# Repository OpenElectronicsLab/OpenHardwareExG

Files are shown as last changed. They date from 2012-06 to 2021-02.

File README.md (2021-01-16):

The OpenHardwareExG is a platform for ECG, EEG, EMG, ENG, EOG, and evoked potential applications.

[About OpenHardwareExG](http://openelectronicslab.github.io/OpenHardwareExG/)

The schematic can be found at:
[arduino-ads129x-schematic.pdf](./kicad-files/rev1/generated-files/arduino-ads129x-schematic.pdf)

History
-------
The OpenHardwareExG platform was originally developed as part of the
[eeg-mouse](https://github.com/OpenElectronicsLab/eeg-mouse) project.

Licences
--------
Hardware and Hardware Documentation License

CERN Open Hardware Licence

This applies to the kicad-files and scad-files directories.

"Documentation" means schematic diagrams, designs, circuit or circuit
board layouts, mechanical drawings, flow charts and descriptive text,
and other explanatory material that is explicitly stated as being made
available under the conditions of this Licence. The Documentation may be
in any medium, including but not limited to computer files and
representations on paper, film, or any other media.

Software License

GPL v3 or any later version

This applies to the OpenHardwareExG_firmware and src directories.

(The authors may be persuaded to license parts of their contributions
under another FOSS license if GPLv3 is a problem for integration with an
existing established project, for instance linux kernel is GPLv2. Please
contact us.)

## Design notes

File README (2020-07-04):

The OpenHardwareExG is a platform for ECG, EEG, EMG, ENG, EOG, and evoked potential applications.

http://openelectronicslab.github.io/OpenHardwareExG/

The OpenHardwareExG platform was originally developed as part of the eeg-mouse project.
https://github.com/OpenElectronicsLab/eeg-mouse

Software License

GPL v3 or any later version

(The authors may be persuaded to license parts of their contributions
under another FOSS license if GPLv3 is a problem for integration with an
existing established project, for instance linux kernel is GPLv2. Please
contact us.) Hardware and Hardware Documentation License

CERN Open Hardware Licence

(This applies mostly to the kicad-files and scad-files directories)
"Documentation" means schematic diagrams, designs, circuit or circuit
board layouts, mechanical drawings, flow charts and descriptive text,
and other explanatory material that is explicitly stated as being made
available under the conditions of this Licence. The Documentation may be
in any medium, including but not limited to computer files and
representations on paper, film, or any other media.

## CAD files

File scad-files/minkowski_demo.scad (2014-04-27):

// This demonstrates why we need to "translate" the origin of a rectangle
// before we apply a minkowski() transformation

// a rectangle with rounded corners of radius r
module rounded_rectangle(size = [1, 1], r = 0.1) {
    // move the origin, to compensate for shrinkage
    // comment out the translate to see the difference
    translate([r,r])

    minkowski() {
        square(size - 2*[r,r]);
        circle(r);
    }
}

$fn = 360;

rect= [3,5];

translate([3.1,0])
square(rect);

rounded_rectangle(rect, 1);

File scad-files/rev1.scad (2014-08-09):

// This file describes a rough 3d model of an OpenHardwareExG board with the
// analog and digital patch shields, along with the plastic fasteners used to
// hold the stack of boards together.  When run directly (vs included with
// "use") it will render the stack of rev1 boards.

include <rev1_dimensions.scad>

// a hexagonal prism with a distance d between sides
// handy for hex nuts
module hexprism(d=1, h=1) {
    $fn=6;
    cylinder(r=d/cos(30)/2, h=h);
}

// a hollow cylinder
module pipe(rout, rin, h) {
    difference() {
        cylinder(r=rout, h=h);
        translate([0, 0, -fudge]) cylinder(r=rin, h=h+2*fudge);
    }
}

// a plastic spacer between boards
module spacer() {
    black_plastic_color()
    pipe(spacer_outer_radius, spacer_inner_radius, spacer_height);
}

// a washer
module washer() {
    black_plastic_color()
    pipe(washer_outer_radius, washer_inner_radius, washer_height);
}

// a hex nut
module nut() {
    black_plastic_color()
    difference() {
        hexprism(d=nut_width, h=nut_height);
        translate([0, 0, -fudge])
            cylinder(r=nut_inner_radius, h=nut_height+2*fudge);
    }
}

// a socket-headed cap screw
module cap_screw(length = cap_screw_body_length) {
    black_plastic_color() {
        translate([0, 0, -cap_screw_cap_height])
        difference() {
            cylinder(r=cap_screw_cap_radius, h=cap_screw_cap_height);
            translate([0, 0, -1/3 * cap_screw_cap_height])
                hexprism(d=cap_screw_hex_key, h=cap_screw_cap_height);
        }
        cylinder(r=cap_screw_body_radius, h=length);
    }
}

// a touch-proof connector
module touch_proof_connector(_x, _y) {
    x = ( in1p_center_x + (_x * distance_between_touchproof_centers));
    y = ( in1p_center_y + (_y * distance_between_touchproof_centers));
    translate([x,y,-touchproof_projection])
        pipe(rout=touchproof_outer_radius, rin=touchproof_inner_radius,
            h=touchproof_height);
}

// color of the PCBs
module boardcolor() {
    color([0.3,0.3,0.3]) child();
}

// color of the black plastic components
module black_plastic_color() {
    for (i = [0 : $children-1])
        color([0.2,0.2,0.2]) child(i);
}

module drilled_hole(radius, x, y)
{
    translate([ x, y ])
        circle(r=radius);
}

module screw_hole(_x,_y)
{
    x = ( screw_hole_centers_x[_x]);
    y = ( screw_hole_centers_y[_y]);
    drilled_hole(screw_hole_radius, x, y);
}

module screw_holes()
{
    for( _y = [ 0 : 1 : 1 ] )
        for( _x = [ 0 : 1 : 3 ] )
            screw_hole(_x, _y);
}

// one of the PCBs
module board() {
    boardcolor() linear_extrude(height=board_thickness)
    difference() {
        square([board_length, board_width]);
        screw_holes();
    }

    // far Arduino headers
    black_plastic_color()
        translate([top_arduino_header_x, top_arduino_header_y,
            -top_arduino_header_height])
        cube([top_arduino_header_length, top_arduino_header_width,
            top_arduino_header_height]);

    // near Arduino headers
    black_plastic_color()
        translate([bottom_arduino_header_x, bottom_arduino_header_y,
            -bottom_arduino_header_height])
        cube([bottom_arduino_header_length, bottom_arduino_header_width,
            bottom_arduino_header_height]);
}

// the top-most PCB
module top_board() {
    board();

    // the touch-proof connectors
    for( _x = [ 0 : 1 : 7 ] ) {
        color([1,0.2,0.2]) touch_proof_connector(_x, 0);
        black_plastic_color() touch_proof_connector(_x, 1);
        black_plastic_color() touch_proof_connector(_x, 2);
        color([0.9,0.9,0.9]) touch_proof_connector(_x, 3);
    }
    color([0.2,0.5,0.2]) touch_proof_connector(8, 1.5);

    // the SPI header cap
    color([0.7,0.7,0.7])
        translate([spi_cap_x, spi_cap_y, -spi_cap_height])
        cube([spi_cap_length, spi_cap_width, spi_cap_height]);
    color([0.7,0.7,0.7])
        translate([spi_cap_tab_x, spi_cap_tab_y, -spi_cap_tab_height])
        cube([spi_cap_tab_length, spi_cap_tab_width, spi_cap_tab_height]);
}

module right_angle_header(pin_count, pitch, length, pin_width) {
    for( i = [ 1 : 1 : pin_count ] ) {
        color([0.9,0.9,0])
            translate([pitch/3,
                (i - 0.5) * pitch - pin_width/2,
                -pitch/2 - pin_width/2])
            cube([length - pitch/3, pin_width, pin_width]);
    }
    black_plastic_color() translate([pitch, 0, -pitch])
        cube([pitch, pin_count * pitch, pitch]);
}

// the bottom-most PCB
module bottom_board() {
    board();

    // USB connector
    color([0.7,0.7,0.7]) translate([USB_x, USB_y, -USB_height])
        difference() {
            cube([USB_length, USB_width, USB_height]);
            translate([USB_length/3, (USB_width - USB_hole_width)/2,
                (USB_height - USB_hole_height)/2])
                cube([USB_length, USB_hole_width, USB_hole_height]);
        }
    black_plastic_color() translate([USB_x, USB_y, -USB_height])
        translate([USB_length/3, (USB_width - USB_post_width)/2,
            (USB_height - USB_post_height)/2])
            cube([2/3*USB_length, USB_post_width, USB_post_height]);

    // FTDI header
    translate([FTDI_x, FTDI_y, 0])
        right_angle_header(FTDI_pin_count, FTDI_pitch, FTDI_length,
            FTDI_pin_width);

    // JYMCU header
    translate([JYMCU_x, JYMCU_y, 0])
        right_angle_header(JYMCU_pin_count, JYMCU_pitch, JYMCU_length,
            JYMCU_pin_width);
}

// the stack of all three boards mounted together
module board_stack() {
    top_board();
    translate([ 0, 0, board_thickness + spacer_height]) board();
    translate([ 0, 0, 2*board_thickness + 2*spacer_height]) bottom_board();
}

module fastener_stack(_x, _y) {
    x = ( screw_hole_centers_x[_x]);
    y = ( screw_hole_centers_y[_y]);
    translate([x,y,-washer_height]) cap_screw();
    translate([x,y,-washer_height]) washer();
    translate([x,y,board_thickness]) spacer();
    translate([x,y,2*board_thickness + spacer_height]) spacer();
    translate([x,y,3*board_thickness + 2*spacer_height]) washer();
    translate([x,y,washer_height + 3*board_thickness + 2*spacer_height]) nut();
}

translate([-board_length/2, board_width/2, 25]) rotate(a=[180,0,0]) {
    // the boards
    board_stack();

    // the fasteners
    for( _y = [ 0 : 1 : 1 ] )
        for( _x = [ 0 : 1 : 3 ] )
            fastener_stack(_x, _y);
}

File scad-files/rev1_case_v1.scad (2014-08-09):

// This file describes a laser-cut case for a rev1 OpenHardwareExG board with the
// analog and digital patch shields.  When run directly (vs included with
// "use") it will render an empty case and a case containing the rev1 boards.

include <rev1_case_v1_dimensions.scad>
use <rev1.scad>

// a rectangle with rounded corners of radius r
module rounded_rectangle(size = [1, 1], r = 0.1) {
    // move the origin, to compensate for shrinkage
    translate([r,r])
    minkowski() {
        square(size - 2*[r,r]);
        circle(r);
    }
}

// color of the case
module case_color() {
    transparency = 0.5;
    for (i = [0 : $children-1])
        color([0.5,0.5,0.7], transparency) child(i);
}

module drilled_slot(x, y, x_len, y_len, r=1)
{
    translate([ x + kerf/2, y + kerf/2 ])
        rounded_rectangle([x_len - kerf, y_len - kerf], r=max(0.01, r-kerf));
}

module drilled_hole(radius, x, y)
{
    translate([ x, y ])
        circle(r=radius - kerf/2);
}

// A slot for a tab, with semicircular cutouts for strain relief in the
// corners.
// note: the center of the slot is at (0,0) (to simplify reasoning about slots
// with different orientations)
module tab_slot(length, width, r_relief) {
    _length = length + tab_slot_length_allowance;
    translate([-_length/2 + kerf/2, -width/2 + kerf/2])
        square([_length - kerf, width - kerf]);
    translate([-_length/2, width/2])
        scale([1,-1]) rotate(90) tab_relief_notch();
    translate([-_length/2, -width/2])
        rotate(90) tab_relief_notch();
    translate([_length/2, width/2])
        rotate(270) tab_relief_notch();
    translate([_length/2, -width/2])
        scale([1,-1]) rotate(270) tab_relief_notch();
}

// A tab
// note: the base of the tab is at (0,0) (to simplify reasoning about tabs with
// different orientations)
module tab(length, width=tab_length, r_corner=tab_corner_radius) {
    union() {
        translate([-length/2 - kerf/2, -fudge]) {
            rounded_rectangle([length + kerf, width + kerf + fudge], r_corner);
            // square out the corners at the attachment point
            square([length + kerf, fudge + r_corner]);
        }
    }
}

// Relief cut outs for a tab.  These should be subtracted from the base part to
// minimize sharp interior angles that can concentrate stress and start crack
// formation.
module tab_relief(length) {
    union() {
        translate([-length/2, 0])
            scale([-1,-1]) tab_relief_notch();
        translate([length/2, 0])
            scale([1,-1]) tab_relief_notch();
    }
}

module tab_relief_notch() {
    difference() {
        union() {
            translate([kerf/2, -kerf/2 - fudge])
                square([(tab_relief_radius * 3) - kerf,
                        tab_relief_radius + kerf/2 + fudge]);
            translate([tab_relief_radius, tab_relief_radius])
                circle(tab_relief_radius - kerf/2);
        }
        translate([tab_relief_radius * 3, tab_relief_radius])
            circle(tab_relief_radius + kerf/2);
    }
}

module touch_proof_hole(_x, _y)
{
    x = ( in1p_center_x + (_x * distance_between_touchproof_centers));
    y = ( in1p_center_y + (_y * distance_between_touchproof_centers));
    drilled_hole(touchproof_outer_radius + touchproof_allowance/2, x, y);
}

module touch_proof_holes()
{
    for( _y = [ 0 : 1 : 3 ] )
        for( _x = [ 0 : 1 : 7 ] )
            touch_proof_hole(_x, _y);
    touch_proof_hole(8, 1.5);
}

module screw_hole(_x,_y)
{
    x = ( screw_hole_centers_x[_x]);
    y = ( screw_hole_centers_y[_y]);
    drilled_hole(screw_hole_radius, x, y);
}

module screw_holes()
{
    for( _y = [ 0 : 1 : 1 ] )
        for( _x = [ 0 : 1 : 3 ] )
            screw_hole(_x, _y);
}

module modified_android_shield_slots()
{
    drilled_slot(top_arduino_header_x - header_allowance/2,
        top_arduino_header_y - header_allowance/2,
        top_arduino_header_length + header_allowance,
        top_arduino_header_width + header_allowance,
        r=header_allowance/2);
    drilled_slot(bottom_arduino_header_x - header_allowance/2,
        bottom_arduino_header_y - header_allowance/2,
        bottom_arduino_header_length + header_allowance,
        bottom_arduino_header_width + header_allowance,
        r=header_allowance/2);
    drilled_slot(spi_cap_x - header_allowance/2,
        spi_cap_y - header_allowance/2,
        spi_cap_length + header_allowance,
        spi_cap_width + header_allowance,
        r=header_allowance/2);
    drilled_slot(spi_cap_tab_x - header_allowance/2,
        spi_cap_tab_y - header_allowance/2,
        spi_cap_tab_length + header_allowance,
        spi_cap_tab_width + header_allowance,
        r=header_allowance/2);
}

module vent_grid(length, width) {
    x_step = ((vent_radius*2) + vent_spacing);
    y_step = ((sqrt(3)/2) * ((vent_radius*2) + vent_spacing));

    num_x = 1 + floor((length - (vent_radius*2)) / x_step );
    num_y = 1 + floor((width - (vent_radius*2)) / y_step );
    translate([(length - (x_step * (num_x-1)))/2,
               (width  - (y_step * (num_y-1)))/2 ])
    for (j = [0 : num_y-1]) {
        for (i = [0 : num_x - 1 - (j - 2*floor(j / 2))]) {
            translate([(j - 2*floor(j / 2)) * (x_step/2), 0])
                translate([i * x_step, j * y_step])
                    circle(vent_radius - (kerf/2));
        }
    }
}

direction_x = [1,0];
direction_y = [0,1];

// Places children and the centers of a line of tabs starting from [0,0] and
// extending to a distance of length in direction direction.
module at_tab_centers(length, direction=direction_x) {
    // fit as many tabs as possible (assuming a gap on each side of the tabs)
    num_tabs = floor((length - tab_width) / (2*tab_width));
    // subtract out the tab widths to find the gap width.
    gap_width = (length - tab_width * num_tabs) / (num_tabs + 1);
    for (j = [0 : num_tabs-1]) {
        translate(direction*(gap_width + tab_width/2 + j*(tab_width + gap_width))) {
            for (i = [0 : $children-1]) {
                child(i);
            }
        }
    }
}

// the top/bottom with their shared holes
module top_blank() {
    difference() {
        translate([-case_top_margin - kerf/2, -case_top_margin - kerf/2])
            rounded_rectangle([ case_top_length + kerf, case_top_width + kerf ],
                case_top_corner_radius + kerf/2);
        screw_holes();

        // top row of tab slots
        translate([-air_gap, -air_gap - acrylic_thickness/2])
            at_tab_centers(board_length + 2 * air_gap, direction_x)
            tab_slot(tab_width,tab_slot_width,tab_slot_relief_radius);

        // bottom row of tab slots
        translate([-air_gap, board_width + air_gap + acrylic_thickness/2])
            at_tab_centers(board_length + 2 * air_gap, direction_x)
            tab_slot(tab_width,tab_slot_width,tab_slot_relief_radius);

        // left row of tab slots
        translate([-air_gap - acrylic_thickness/2, -case_top_margin])
            at_tab_centers(case_top_width, direction_y)
            rotate(90) tab_slot(tab_width,tab_slot_width,tab_slot_relief_radius);

        // right row of tab slots
        translate([ board_length + air_gap + acrylic_thickness/2,
            -case_top_margin])
            at_tab_centers(case_top_width, direction_y)
            rotate(90) tab_slot(tab_width,tab_slot_width,tab_slot_relief_radius);
    }
}

// the bottom
module bottom() {
    difference() {
        top_blank();
        translate([vent_bottom_margin,vent_bottom_margin])
        vent_grid(board_length - (2*vent_bottom_margin),
                         board_width - (2*vent_bottom_margin));
    }
}

// the top
module top() {
    difference() {
        top_blank();
        touch_proof_holes();
        modified_android_shield_slots();
    }
}

module front() {
    difference() {
        union() {
            // the basic rectangle
            translate([ -air_gap - kerf/2, - kerf/2])
                rounded_rectangle([ case_front_length + kerf,
                    case_front_width + kerf ],
                    case_front_corner_radius + kerf/2);

            // top tabs
            translate([-air_gap, 0])
                at_tab_centers(board_length + 2 * air_gap, direction_x)
                rotate(180) tab(tab_width, tab_length+compression_gap);

            // bottom tabs
            translate([-air_gap, case_front_width])
                at_tab_centers(board_length + 2 * air_gap, direction_x)
                tab(tab_width);

            // left tabs
            translate([-air_gap,
                       (-compression_gap/2)+(-tab_slot_length_allowance/4)])
                at_tab_centers(case_front_width, direction_y)
                rotate(90) tab(tab_width);

            // right tabs
            translate([board_length + air_gap,
                       (-compression_gap/2)+(-tab_slot_length_allowance/4)])
                at_tab_centers(case_front_width, direction_y)
                rotate(270) tab(tab_width);
        }
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

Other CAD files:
scad-files/rev1_case_v1_dimensions.scad
scad-files/rev1_case_v1_pattern.scad
scad-files/rev1_case_v1_pattern_P2.scad
scad-files/rev1_dimensions.scad

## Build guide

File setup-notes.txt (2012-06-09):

need to install the perl module Device/SerialPort.pm

    sudo apt-get install libdevice-serialport-perl

need to verify the /dev/ttyACM0 (or adjust serial-reader.pl to match)

need to have rights to tty device ("dialout" group on ubuntu)

sudo apt-get install gnuplot

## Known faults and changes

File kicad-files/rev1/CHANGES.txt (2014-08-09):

If you are distributing a modified version of the project, please use this file
to describe the dates and details of your modifications (as described in
section 3.3b of the CERN open hardware license).  If you are using a publicly
available repository to track changes (which we encourage), you may simply list
the URL of the repository here.

https://github.com/OpenElectronicsLab/OpenHardwareExG

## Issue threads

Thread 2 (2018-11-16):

### ISSUE TITLE
BoM list

### ISSUE THREAD

**Issue by hildogjr** [OpenElectronicsLab/OpenHardwareExG#2]
Missing some BoM list with the part number to make easy the purchase procedure.

**Comment by ericherman** [comment]
You can see a number of ".bom" files in the project. Probably you're interested in the main board, with the analog+digital patch shields:

 * https://github.com/OpenElectronicsLab/OpenHardwareExG/blob/master/kicad-files/rev1/arduino-ads129x.bom
 * https://github.com/OpenElectronicsLab/OpenHardwareExG/blob/master/kicad-files/rev1/patch-shield-analog.bom
 * https://github.com/OpenElectronicsLab/OpenHardwareExG/blob/master/kicad-files/rev1/patch-shield-digital.bom

Since there are multiple boards, we made a "combined mouser bom" for the patch-shield version for ordering from mouser:
 * https://github.com/OpenElectronicsLab/OpenHardwareExG/blob/master/kicad-files/rev1/combined.mouser.bom

However, not all parts were available from mouser at the time, as such we created a 4ucon bom:
 * https://github.com/OpenElectronicsLab/OpenHardwareExG/blob/master/kicad-files/rev1/4ucon.bom

Additionally, for the touch-proof panel mount jacks, we found them at DiscountDisposables as documented in:
 * https://github.com/OpenElectronicsLab/OpenHardwareExG/blob/master/kicad-files/rev1/fasteners.txt

I hope this is helpful for you.

**Comment by hildogjr** [comment]
Thanks

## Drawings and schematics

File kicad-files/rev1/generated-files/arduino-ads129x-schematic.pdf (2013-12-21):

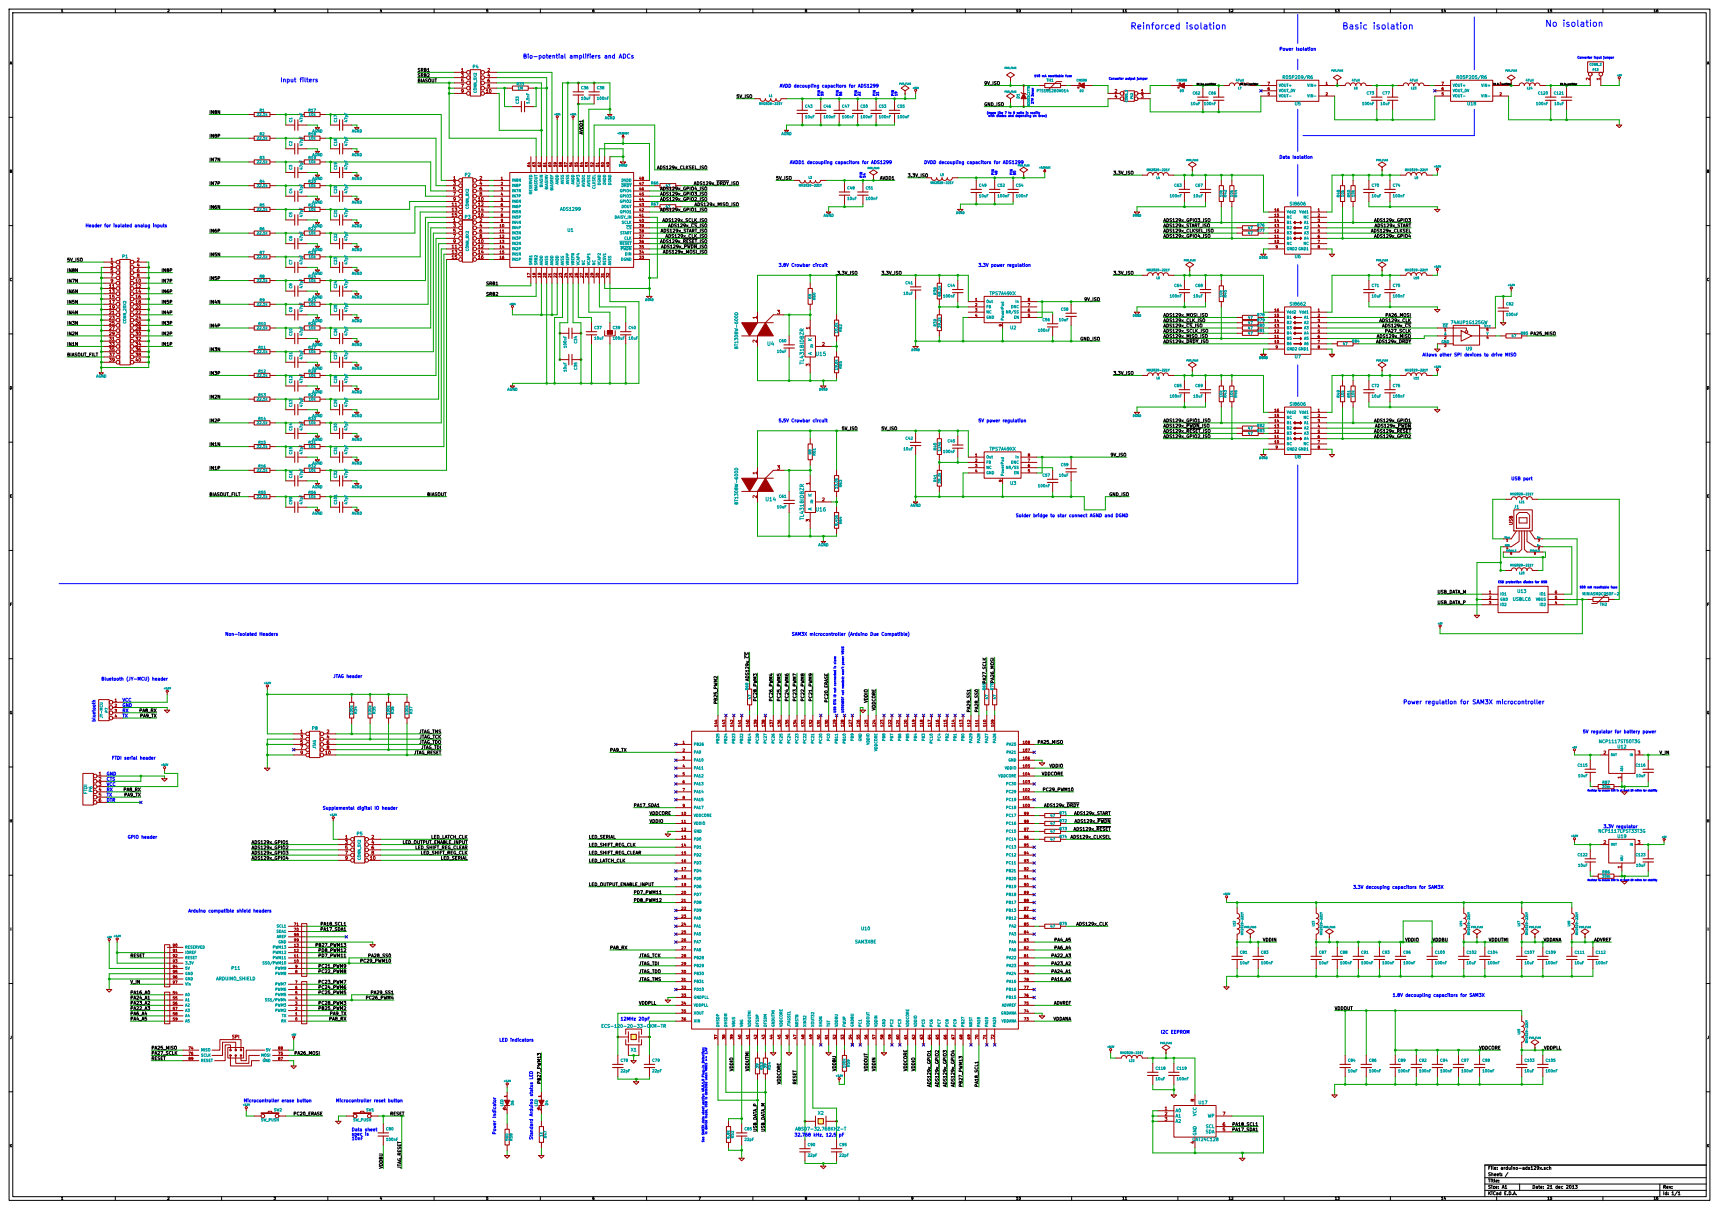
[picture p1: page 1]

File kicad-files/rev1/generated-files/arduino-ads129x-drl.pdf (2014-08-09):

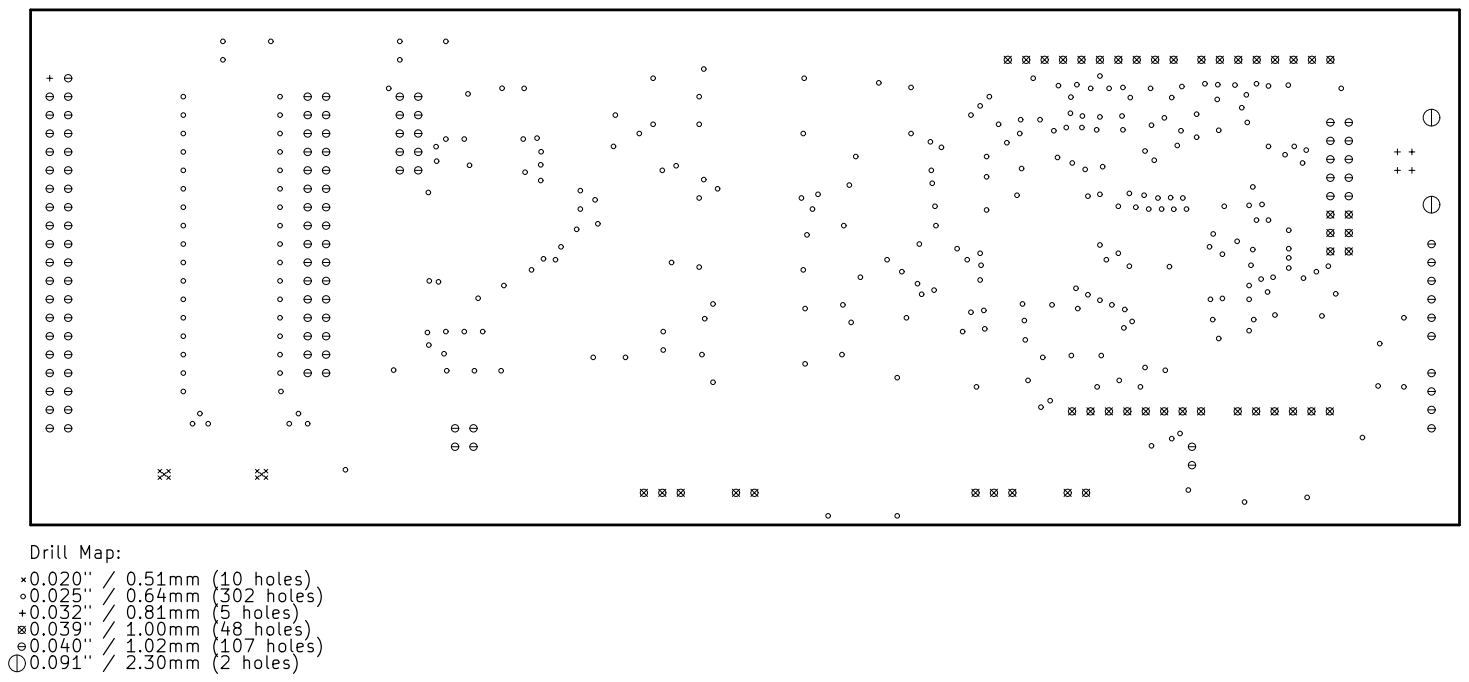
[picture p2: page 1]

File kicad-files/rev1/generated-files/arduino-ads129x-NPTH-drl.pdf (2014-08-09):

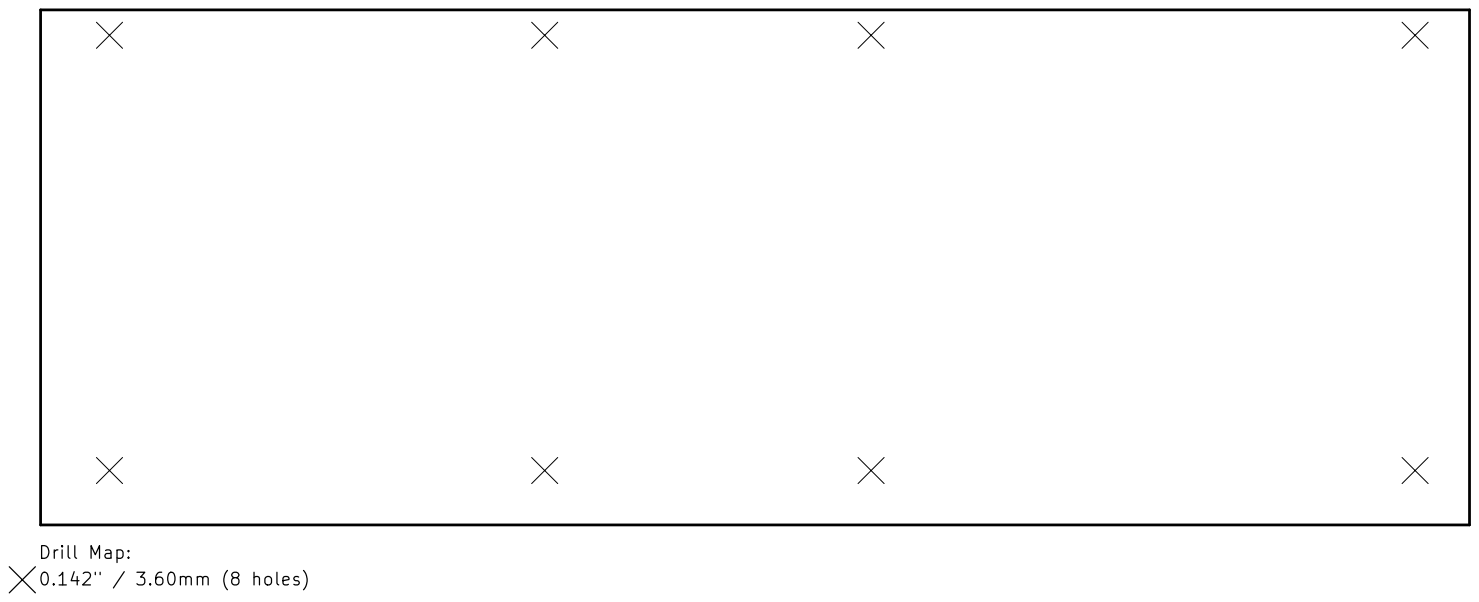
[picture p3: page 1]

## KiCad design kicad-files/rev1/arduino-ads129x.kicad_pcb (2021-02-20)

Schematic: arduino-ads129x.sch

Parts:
C1, C2, C3, C4, C5, C6, C7, C8, C9, C10, C11, C12, C13, C14, C15, C16, C17, C18, C19, C20, C21, C22, C23, C24, C25, C26, C27, C28, C29, C30, C31, C32, C99, C101: 270pF; SM0603
C33: 1.5nF; SM0603
C34, C38, C44, C45, C46, C47, C50, C51, C52, C53, C54, C55, C56, C57, C63, C64, C65, C66, C73, C74, C75, C76, C80, C82, C83, C86, C88, C89, C91, C92, C93, C94, C96, C97, C98, C100, C104, C105, C109, C112, C119, C120: 100nF; SM0603
C35, C36, C37, C40, C41, C42, C43, C48, C49, C60, C61, C67, C68, C69, C70, C71, C72, C77, C81, C84, C87, C102, C103, C107, C111, C115, C118, C121, C122, C123: 10uF; SM0805
C39: 100uF; SM2512
C58, C59, C62, C116: 10uF; SM1210
C78, C79, C85, C90, C95: 22pF; SM0603
D1: BZG03C27TR; DO214
D2, D3: CMS06; SM2010
D4, D6: LED; LED-0603
J1: USB; USB_B
L1, L2, L3, L4, L5, L6, L9, L10, L11, L12, L13, L14, L15, L17, L18, L20, L21, L22: MH2029-221Y; SM0805
L7, L8, L23, L24: 47uH; SRR4028
P1: CONN_20X2; PIN_ARRAY_20X2
P2, P3: CONN_8X2; pin_array_8x2
P4, P5: CONN_5X2; PIN_ARRAY_5x2
P6: FTDI; PIN_ARRAY-6X1
P7: JY-MCU; PIN_ARRAY_4x1
P8: JTAG; SMT_PIN_2x5
P11: ARDUINO_SHIELD; arduino_shield
P12: CONN_2; PIN_ARRAY_2X2
P13: CONN_2; PIN_ARRAY_2X1
R1, R2, R3, R4, R5, R6, R7, R8, R9, R10, R11, R12, R13, R14, R15, R16, R17, R18, R19, R20, R21, R22, R23, R24, R25, R26, R27, R28, R29, R30, R31, R32, R55, R56: 2.61k; SM0603
R33: 1M; SM0805
R34, R35, R36, R37, R59: 100k; SM0603
R38: 68.1k; SM0603
R39, R41: 39.2k; SM0603
R40: 124k; SM0603
R42, R43, R44, R45, R46, R48, R49, R50, R51: 10k; SM0603
R47: 1k; SM0603
R52: 6.8k; SM0603
R53, R54: 39; SM0603
R58: 560; SM0603
R60, R61: 68; SM0603
R62, R63: 10.0k; SM0603
R64: 8.45k; SM0603
R65: 19.6k; SM0603
R66, R67, R68, R69, R70, R71, R72, R73, R74, R75, R76, R77, R78, R79, R80, R81, R82, R83, R84, R85: 47; SM0603
R86, R87: 30m; SM0603
SW1, SW2: SW_PUSH; smt-tactile-button
TH1: PTS181260V014; SM1812
TH2: MINIASMDC050F-2; SM1812
U1: ADS1299; TQFP_64
U2, U3: TPS7A49XX; MSOP8_PowerPad
U4, U14: BT1308W-600D; SOT223
U5: R05P209/R6; SIP7_ISOLATOR
U6, U8: SI8606; SO16W
U7: SI8662; SO16W
U9: 74AUP1G125GW; SOT353
U10: SAM3X8E; TQFP144
U12: NCP1117ST50T3G; SOT223
U13: USBLC6; SOT23_6
U15, U16: TL431BIDBZR; SOT23
U17: CAT24C128; SOIC8
U18: R05P205/R6; SIP7_ISOLATOR
U19: NCP1117LPST33T3G; SOT223
X1: ECS-120-20-33-CKM-TR; smt-crystal-3.2x2.5
X2: ABS07-32.768KHZ-T; ABS07

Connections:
+3.3V: C82.1, C122.1, D6.1 (A), L9.2, L10.2, L11.2, L12.1, L13.1, L14.1, L17.1, L18.1, L22.1, P5.1, P6.3, P7.1, P8.1, P11.91, P11.93, R34.1, R35.1, R36.1, R37.1, R59.2, SW2.1, U9.5 (Vcc), U19.2 (OUT)
/3.3V_ISO: C41.1, C44.1, L3.2, L4.2, L5.2, L6.2, R38.1, R60.1, R62.1, U2.1 (Out), U4.1
/5V_ISO: C42.1, C45.1, L1.2, L2.2, P1.1, R40.1, R61.1, R63.1, U3.1 (Out), U14.1
/5V_in_prefilter: C120.1, C121.1, L24.1, P13.2 (PM)
/9V_ISO: C58.1, C59.1, D1.2 (K), TH1.1, U2.5 (EN), U2.8 (In), U3.5 (EN), U3.8 (In)
/9V_iso_postfilter: C62.1, C66.1, D3.1 (A), L7.2
/ADS129x_CLK: R75.2, U7.3 (A2)
/ADS129x_CLKSEL: R74.2, U6.5 (A3)
/ADS129x_CLKSEL_ISO: R77.1, U1.52 (CLKSEL)
/ADS129x_CLK_ISO: R79.1, U1.37 (CLK)
/ADS129x_GPIO1: P5.3, R51.2, U8.3 (A1), U10.64 (PC6)
/ADS129x_GPIO1_ISO: R43.2, U1.42 (GPIO1), U8.14 (B1)
/ADS129x_GPIO2: P5.5, R49.2, U8.6 (A4), U10.65 (PC7)
/ADS129x_GPIO2_ISO: R46.2, U1.44 (GPIO2), U8.11 (B4)
/ADS129x_GPIO3: P5.7, R50.2, U6.3 (A1), U10.66 (PC8)
/ADS129x_GPIO3_ISO: R42.2, U1.45 (GPIO3), U6.14 (B1)
/ADS129x_GPIO4: P5.9, R48.2, U6.6 (A4), U10.67 (PC9)
/ADS129x_GPIO4_ISO: R44.2, U1.46 (GPIO4), U6.11 (B4)
/ADS129x_MISO: U7.6 (A5), U9.2 (A)
/ADS129x_MISO_ISO: R45.2, R67.2, U7.11 (B5)
/ADS129x_MOSI_ISO: R78.1, U1.34 (DIN)
/ADS129x_SCLK_ISO: R81.1, U1.40 (SCLK)
/ADS129x_START: R71.2, U6.4 (A2)
/ADS129x_START_ISO: R76.1, U1.38 (START)
/ADS129x_~CS~: R68.2, U7.4 (A3), U9.1 (~OE~)
/ADS129x_~CS~_ISO: R80.1, U1.39 (~CS~)
/ADS129x_~DRDY~: R84.2, U10.100 (PC18)
/ADS129x_~DRDY~_ISO: R66.2, U7.10 (B6)
/ADS129x_~PWDN~: R72.2, U8.4 (A2)
/ADS129x_~PWDN~_ISO: R82.1, U1.35 (~PWDN~)
/ADS129x_~RESET~: R73.2, U8.5 (A3)
/ADS129x_~RESET~_ISO: R83.1, U1.36 (~RESET~)
/ADVREF: C111.1, C112.1, L18.2, U10.75 (ADVREF)
/AVDD1: C48.1, C51.1, L2.1, U1.54 (AVDD1)
/BIASOUT: C101.1, P4.5, P4.7, P4.9, R56.2, U1.63 (BIASOUT)
/BIASOUT_FILT: P1.37, R55.1
/IN1N: P1.33, R15.1
/IN1P: P1.34, R16.1
/IN2N: P1.29, R13.1
/IN2P: P1.30, R14.1
/IN3N: P1.25, R11.1
/IN3P: P1.26, R12.1
/IN4N: P1.21, R9.1
/IN4P: P1.22, R10.1
/IN5N: P1.17, R7.1
/IN5P: P1.18, R8.1
/IN6N: P1.13, R5.1
/IN6P: P1.14, R6.1
/IN7N: P1.9, R3.1
/IN7P: P1.10, R4.1
/IN8N: P1.5, R1.1
/IN8P: P1.6, R2.1
/JTAG_RESET: C80.1, P8.10, P11.89, P11.92, R37.2, SW1.2, U10.47 (NRSTB)
/JTAG_TCK: P8.4, R35.2, U10.28 (PB28)
/JTAG_TDI: P8.8, R36.2, U10.29 (PB29)
/JTAG_TDO: P8.6, U10.30 (PB30)
/JTAG_TMS: P8.2, R34.2, U10.31 (PB31)
/LED_LATCH_CLK: P5.2, U10.16 (PD3)
/LED_OUTPUT_ENABLE_INPUT: P5.4, U10.19 (PD6)
/LED_SERIAL: P5.10, U10.13 (PD0)
/LED_SHIFT_REG_CLEAR: P5.6, U10.15 (PD2)
/LED_SHIFT_REG_CLK: P5.8, U10.14 (PD1)
/PA4_A5: P11.59, U10.83 (PA4)
/PA6_A4: P11.58, U10.82 (PA6)
/PA8_RX: P6.4, P7.3, P11.0, U10.27 (PA8)
/PA9_TX: P6.5, P7.4, P11.1, U10.2 (PA9)
/PA16_A0: P11.54, U10.78 (PA16)
/PA17_SDA1: P11.70, U10.9 (PA17), U17.5 (SDA)
/PA18_SCL1: P11.71, U10.70 (PA18), U17.6 (SCL)
/PA22_A3: P11.57, U10.81 (PA22)
/PA23_A2: P11.56, U10.80 (PA23)
/PA24_A1: P11.55, U10.79 (PA24)
/PA25_MISO: P11.74, R85.2, U10.108 (PA25)
/PA26_MOSI: P11.75, R70.2, U7.2 (A1)
/PA27_SCLK: P11.76, R69.2, U7.5 (A4)
/PA28_SS0: P11.10, U10.102 (PC29), U10.111 (PA28)
/PA29_SS1: P11.4, U10.112 (PA29), U10.137 (PC26)
/PB25_PWM2: P11.2, U10.144 (PB25)
/PB27_PWM13: D4.1 (A), P11.13, U10.68 (PB27)
/PC20_ERASE: SW2.2, U10.130 (PC0)
/PC21_PWM9: P11.9, U10.132 (PC21)
/PC22_PWM8: P11.8, U10.133 (PC22)
/PC23_PWM7: P11.7, U10.134 (PC23)
/PC24_PWM6: P11.6, U10.135 (PC24)
/PC25_PWM5: P11.5, U10.136 (PC25)
/PC28_PWM3: P11.3, U10.139 (PC28)
/PD7_PWM11: P11.11, U10.20 (PD7)
/PD8_PWM12: P11.12, U10.21 (PD8)
/SRB1: P4.1, U1.17 (SRB1)
/SRB2: P4.3, U1.18 (SRB2)
/USB_DATA_M: R54.2, U10.38 (DHSDM), U13.1 (IO1)
/USB_DATA_P: R53.2, U10.37 (DHSDP), U13.3 (IO2)
/VDDANA: C107.1, C109.1, L17.2, U10.73 (VDDANA)
/VDDBU: C80.2, C87.1, C88.1, C91.1, C93.1, C96.1, C100.1, L13.2, U10.11 (VDDIO), U10.39 (VBUS), U10.52 (VDDBU), U10.62 (VDDIO), U10.105 (VDDIO), U10.125 (VDDIO)
/VDDCORE: C84.1, C86.1, C89.1, C92.1, C94.1, C97.1, C98.1, L15.1, U10.10 (VDDCORE), U10.45 (VDDCORE), U10.56 (VDDOUT), U10.61 (VDDCORE), U10.104 (VDDCORE), U10.124 (VDDCORE)
/VDDIN: C81.1, C83.1, L12.2, U10.57 (VDDIN)
/VDDPLL: C103.1, C105.1, L15.2, U10.34 (VDDPLL)
/VDDUTMI: C102.1, C104.1, L14.2, U10.41 (VDDUTMI)
/V_IN: C116.1, P11.97, U12.3 (IN)
AGND: C1.2, C2.2, C3.2, C4.2, C5.2, C6.2, C7.2, C8.2, C9.2, C10.2, C11.2, C12.2, C13.2, C14.2, C15.2, C16.2, C17.2, C18.2, C19.2, C20.2, C21.2, C22.2, C23.2, C24.2, C25.2, C26.2, C27.2, C28.2, C29.2, C30.2, C31.2, C32.2, C34.1, C35.1, C36.1, C37.2, C38.1, C39.2, C40.2, C41.2, C42.2, C43.2, C46.2, C47.2, C48.2, C49.2, C50.2, C51.2, C52.2, C53.2, C54.2, C55.2, C56.2, C57.2, C58.2, C59.2, C60.2, C61.2, C63.2, C64.2, C65.2, C67.2, C68.2, C69.2, C99.2, C101.2, D1.1 (A), P1.2, P1.3, P1.4, P1.7, P1.8, P1.11, P1.12, P1.15, P1.16, P1.19, P1.20, P1.23, P1.24, P1.27, P1.28, P1.31, P1.32, P1.35, P1.36, P1.38, P1.39, P1.40, P12.4, R39.2, R41.2, R64.2, R65.2, U1.20 (AVSS), U1.23 (AVSS), U1.25 (VREFN), U1.31 (RESV1), U1.32 (AVSS), U1.33 (DGND), U1.41 (DAISY_IN), U1.49 (DGND), U1.51 (DGND), U1.53 (AVSS1), U1.57 (AVSS), U1.58 (AVSS), U2.4 (GND), U2.9 (PowerPad), U3.4 (GND), U3.9 (PowerPad), U4.2, U6.9 (GND2), U7.9 (GND2), U8.9 (GND2), U14.2, U15.3 (A), U16.3 (A)
GND: C70.2, C71.2, C72.2, C74.2, C75.2, C76.2, C78.2, C79.2, C81.2, C82.2, C83.2, C84.2, C85.2, C86.2, C87.2, C88.2, C89.2, C90.2, C91.2, C92.2, C93.2, C94.2, C95.2, C96.2, C97.2, C98.2, C100.2, C102.2, C103.2, C104.2, C105.2, C107.2, C109.2, C111.2, C112.2, C116.2, C118.2, C119.2, C120.2, C121.2, C123.2, J1.4 (GND), L20.1, P6.1, P6.2, P7.2, P8.3, P8.5, P8.9, P11.87, P11.95, P11.96, P11.99, R47.2, R52.2, R58.2, R86.1, R87.1, SW1.1, U6.8 (GND1), U7.8 (GND1), U8.8 (GND1), U9.3 (GND), U10.12 (GND), U10.33 (GNDPLL), U10.44 (GNDUTMI), U10.46 (JTAGSEL), U10.51 (TST), U10.58 (GND), U10.74 (GNDANA), U10.106 (GND), U10.126 (GND), U12.1 (ADJ), U13.2 (GND), U17.1 (A0), U17.2 (A1), U17.3 (A2), U17.4 (GND), U17.7 (WP), U18.2 (VIN-), U19.1 (ADJ), X1.2 (GND1), X1.4 (GND2)
unnamed: C72.1, C76.1, L11.1, R49.1, R51.1, U8.1 (Vdd1)
unnamed: C65.1, C69.1, L6.1, R43.1, R46.1, U8.16 (Vdd2)
unnamed: C64.1, C68.1, L5.1, R45.1, U7.16 (Vdd2)
unnamed: C45.2, R40.2, R41.1, U3.2 (FB)
unnamed: C56.1, U2.6 (NR/SS)
unnamed: C57.1, U3.6 (NR/SS)
unnamed: C63.1, C67.1, L4.1, R42.1, R44.1, U6.16 (Vdd2)
unnamed: C118.1, C119.1, L22.2, U17.8 (VCC)
unnamed: L24.2, U18.1 (VIN+)
unnamed: P4.6, P4.10, U1.62 (BIASIN)
unnamed: R62.2, R65.1, U15.2 (R)
unnamed: C60.1, R60.2, U4.3, U15.1 (K)
unnamed: C79.1, U10.36 (XIN), X1.3
unnamed: D3.2 (K), P12.1
unnamed: P4.2, U1.60 (BIASREF)
unnamed: J1.3 (D+), U13.4 (IO2)
unnamed: D4.2 (K), R47.1
unnamed: C14.1, R14.2, R30.1
unnamed: C25.1, P3.1, R25.2
unnamed: C9.1, R9.2, R25.1
unnamed: C24.1, P2.15, R24.2
unnamed: C8.1, R8.2, R24.1
unnamed: C31.1, P3.13, R31.2
unnamed: C15.1, R15.2, R31.1
unnamed: C39.1, U1.28 (VCAP1)
unnamed: C33.1, P4.8, R33.1
unnamed: C28.1, P3.7, R28.2
unnamed: C40.1, U1.30 (VCAP2)
unnamed: P2.10, U1.5 (IN6N)
unnamed: C20.1, P2.7, R20.2
unnamed: P2.12, U1.6 (IN6P)
unnamed: P2.14, U1.7 (IN5N)
unnamed: P2.16, U1.8 (IN5P)
unnamed: P2.2, U1.1 (IN8N)
unnamed: P2.4, U1.2 (IN8P)
unnamed: P2.6, U1.3 (IN7N)
unnamed: P2.8, U1.4 (IN7P)
unnamed: R66.1, U1.47 (~DRDY~)
unnamed: J1.1 (Vbus), L21.1
unnamed: J1.2 (D-), U13.6 (IO1)
unnamed: R67.1, U1.43 (DOUT)
unnamed: C34.2, C35.2, U1.24 (VREFP)
unnamed: C36.2, C38.2, U1.55 (VCAP3)
unnamed: P3.16, U1.16 (IN1P)
unnamed: C37.1, U1.26 (VCAP4)
unnamed: C18.1, P2.3, R18.2
unnamed: C2.1, R2.2, R18.1
unnamed: C21.1, P2.9, R21.2
unnamed: C5.1, R5.2, R21.1
unnamed: C17.1, P2.1, R17.2
unnamed: P3.4, U1.10 (IN4P)
unnamed: P3.2, U1.9 (IN4N)
unnamed: C26.1, P3.3, R26.2
unnamed: P3.6, U1.11 (IN3N)
unnamed: P3.8, U1.12 (IN3P)
unnamed: P3.10, U1.13 (IN2N)
unnamed: C30.1, P3.11, R30.2
unnamed: P3.12, U1.14 (IN2P)
unnamed: P3.14, U1.15 (IN1N)
unnamed: C19.1, P2.5, R19.2
unnamed: C3.1, R3.2, R19.1
unnamed: C73.1, C77.1, L8.1, L23.2
unnamed: L7.1, U5.7 (VOUT+)
unnamed: C73.2, C77.2, U5.2 (VIN-), U18.5 (VOUT-)
unnamed: J1.5 (Shield_1), J1.6 (Shield_2), L20.2
unnamed: D2.1 (A), P12.2
unnamed: L21.2, TH2.1
unnamed: C90.1, U10.48 (XIN32), X2.1
unnamed: D6.2 (K), R58.1
unnamed: D2.2 (K), TH1.2
unnamed: C85.1, R52.1, U10.40 (VBG)
unnamed: C95.1, U10.49 (XOUT32), X2.2
unnamed: R72.1, U10.98 (PC16)
unnamed: R71.1, U10.99 (PC17)
unnamed: R69.1, U10.110 (PA27)
unnamed: R68.1, U10.140 (PB14)
unnamed: R75.1, U10.85 (PA2)
unnamed: R74.1, U10.96 (PC14)
unnamed: R73.1, U10.97 (PC15)
unnamed: R54.1, U10.43 (DFSDM)
unnamed: R59.1, U10.53 (FWUP)
unnamed: C78.1, U10.35 (XOUT), X1.1
unnamed: R76.2, U6.13 (B2)
unnamed: R53.1, U10.42 (DFSDP)
unnamed: C4.1, R4.2, R20.1
unnamed: C10.1, R10.2, R26.1
unnamed: C27.1, P3.5, R27.2
unnamed: C11.1, R11.2, R27.1
unnamed: C29.1, P3.9, R29.2
unnamed: C13.1, R13.2, R29.1
unnamed: C12.1, R12.2, R28.1
unnamed: C1.1, R1.2, R17.1
unnamed: C22.1, P2.11, R22.2
unnamed: C6.1, R6.2, R22.1
unnamed: C16.1, R16.2, R32.1
unnamed: C32.1, P3.15, R32.2
unnamed: C23.1, P2.13, R23.2
unnamed: C7.1, R7.2, R23.1
unnamed: C99.1, R55.2, R56.1
unnamed: C115.2, R87.2
unnamed: C61.1, R61.2, U14.3, U16.1 (K)
unnamed: R63.2, R64.1, U16.2 (R)
unnamed: C33.2, P4.4, R33.2, U1.61 (BIASINV)
unnamed: C44.2, R38.2, R39.1, U2.2 (FB)
unnamed: R85.1, U9.4 (Y)
unnamed: R84.1, U7.7 (A6)
unnamed: R81.2, U7.12 (B4)
unnamed: R80.2, U7.13 (B3)
unnamed: R78.2, U7.15 (B1)
unnamed: R79.2, U7.14 (B2)
unnamed: R82.2, U8.13 (B2)
unnamed: R83.2, U8.12 (B3)
unnamed: R77.2, U6.12 (B3)
unnamed: C122.2, R86.2
unnamed: L23.1, U18.7 (VOUT+)
unnamed: R70.1, U10.109 (PA26)
unnamed: L8.2, U5.1 (VIN+)
unnamed: C62.2, C66.2, P12.3, U5.5 (VOUT-)
unnamed: C70.1, C74.1, L9.1, R48.1, R50.1, U6.1 (Vdd1)
unnamed: C71.1, C75.1, L10.1, U7.1 (Vdd1)

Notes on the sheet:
Microcontroller erase button
Solder bridge to star connect AGND and DGND
Resistor to ensure ESR is at least 20 mOhm for stability
3.3V regulator
Basic isolation
I2C EEPROM
12MHz 20pF
32.768 kHz, 12.5 pF
Microcontroller reset button
Power regulation for SAM3X microcontroller
SAM3X microcontroller (Arduino Due Compatible)
Standard Arduino status LED
Power Indicator
LED indicators
Non-isolated Headers
Arduino compatible shield headers
Supplemental digital IO header
Bluetooth (JY-MCU) header
FTDI serial header
GPIO header
JTAG header
1.8V decoupling capacitors for SAM3X
3.3V decouping capacitors for SAM3X
USB port
Header for isolated analog inputs
Input filters
Bio-potential amplifiers and ADCs
ESD protection diodes for USB
500 mA resettable fuse
140 mA resettable fuse
27V Zener
bluetooth
3.8V Crowbar circuit
5.5V Crowbar circuit
No isolation
Reinforced isolation
Allows other SPI devices to drive MISO
5V regulator for battery power
PIN 48
PIN 50

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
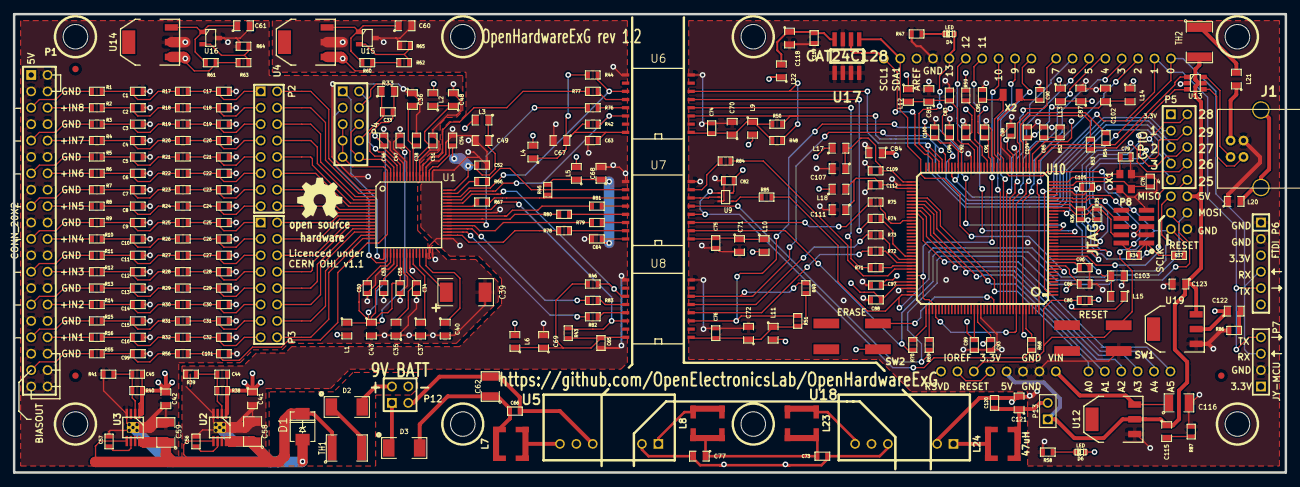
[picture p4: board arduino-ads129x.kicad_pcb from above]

Board: 4 copper layers, 197.0 x 71.0 mm, 277 parts (0 on the bottom side), 224 nets.

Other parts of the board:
Hole_M3, Hole_M3#2, Hole_M3#3, Hole_M3#4, Hole_M3#5, Hole_M3#6, Hole_M3#7, Hole_M3#8: VAL**; Hole_M3
fiducial_mark: VAL**; fiducial_mark
fiducial_mark#2, fiducial_mark#3: VAL**; fiducial_mark

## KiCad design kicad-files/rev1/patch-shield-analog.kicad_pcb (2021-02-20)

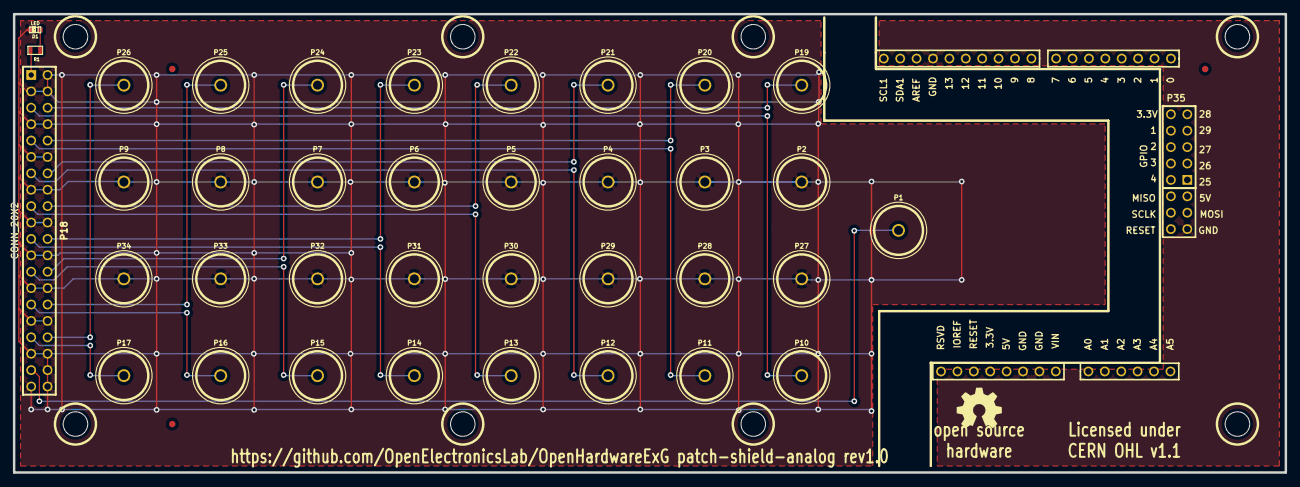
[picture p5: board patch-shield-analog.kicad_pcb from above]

Board: 2 copper layers, 197.0 x 71.0 mm, 49 parts (0 on the bottom side), 21 nets.

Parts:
D1: LED; LED-0603
Hole_M3, Hole_M3#2, Hole_M3#3, Hole_M3#4, Hole_M3#5, Hole_M3#6, Hole_M3#7, Hole_M3#8: VAL**; Hole_M3
P1, P2, P3, P4, P5, P6, P7, P8, P9, P10, P11, P12, P13, P14, P15, P16, P17, P19, P20, P21, P22, P23, P24, P25, P26, P27, P28, P29, P30, P31, P32, P33, P34: CONN_1; Touchproof-socket
P18: CONN_20X2; PIN_ARRAY_20X2
P35: CONN_5X2; PIN_ARRAY_5x2
P36: ARDUINO_SHIELD; arduino_shield
R1: 1k; SM0603
fiducial_mark: VAL**; fiducial_mark
fiducial_mark#2, fiducial_mark#3: VAL**; fiducial_mark

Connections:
+5VA: P18.1, R1.1
/BIASOUT: P1.1, P18.37
/IN1N: P17.1, P18.33
/IN1P: P18.34, P26.1
/IN2N: P16.1, P18.29
/IN2P: P18.30, P25.1
/IN3N: P15.1, P18.25
/IN3P: P18.26, P24.1
/IN4N: P14.1, P18.21
/IN4P: P18.22, P23.1
/IN5N: P13.1, P18.17
/IN5P: P18.18, P22.1
/IN6N: P12.1, P18.13
/IN6P: P18.14, P21.1
/IN7N: P11.1, P18.9
/IN7P: P18.10, P20.1
/IN8N: P10.1, P18.5
/IN8P: P18.6, P19.1
AGND: D1.2, P2.1, P3.1, P4.1, P5.1, P6.1, P7.1, P8.1, P9.1, P18.2, P18.3, P18.4, P18.7, P18.8, P18.11, P18.12, P18.15, P18.16, P18.19, P18.20, P18.23, P18.24, P18.27, P18.28, P18.31, P18.32, P18.35, P18.36, P18.38, P18.39, P18.40, P27.1, P28.1, P29.1, P30.1, P31.1, P32.1, P33.1, P34.1
DGND: P36.87, P36.95, P36.96, P36.99
unnamed: D1.1, R1.2

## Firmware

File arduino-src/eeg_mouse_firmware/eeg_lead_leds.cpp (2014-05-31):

#include <Arduino.h>
#include "eeg_mouse_firmware.h"
#include "eeg_lead_leds.h"

const int num_inputs_per_channel = 2;	// IN1N, IN1P
const int num_leds =
    Eeg_lead_leds::num_channels * num_inputs_per_channel * Eeg_lead_leds::num_colors;
const int states_per_led = 2;	// clock low and high

enum states {
	first_data_state = 0,
	last_data_state = (states_per_led * num_leds) - 1,
	latch_start,		// no value is the same as previous element + 1
	latch_end,
	last_state = latch_end
};

Eeg_lead_leds::Eeg_lead_leds()
{
	leds_state = 0;
	step = 0;
}

void Eeg_lead_leds::begin()
{
	// set up the pins for the LEDs
	pinMode(IPIN_LED_ENABLE, OUTPUT);
	pinMode(PIN_LED_LATCH, OUTPUT);
	pinMode(IPIN_LED_CLEAR, OUTPUT);
	pinMode(PIN_LED_CLK, OUTPUT);
	pinMode(PIN_LED_SERIAL, OUTPUT);

	digitalWrite(PIN_LED_LATCH, LOW);
	digitalWrite(PIN_LED_CLK, LOW);
	digitalWrite(IPIN_LED_ENABLE, LOW);

	// set LEDs to leds_state (probably 0, all off)
	update_all();
}

void Eeg_lead_leds::set_led(led_color color, int channel, polarity pol, bool on)
{
	int led_num = (num_colors * (channel + pol)) + color;
	uint32_t mask = (1 << led_num);

	leds_state = (leds_state & ~mask);
	if (on) {
		leds_state |= mask;
	}
}

void Eeg_lead_leds::set_green_positive(int channel, bool on)
{
	set_led(green, channel, positive, on);
}

void Eeg_lead_leds::set_yellow_positive(int channel, bool on)
{
	set_led(yellow, channel, positive, on);
}

void Eeg_lead_leds::set_green_negative(int channel, bool on)
{
	set_led(green, channel, negative, on);
}

void Eeg_lead_leds::set_yellow_negative(int channel, bool on)
{
	set_led(yellow, channel, negative, on);
}


void Eeg_lead_leds::update_tick()
{
	switch (step) {
	case latch_start:	// this happens almost last (defaults are first)
		// latch the data from the shift register to the LEDs
		digitalWrite(PIN_LED_LATCH, HIGH);
		++step;
		break;

	case latch_end:
		// reset the latch
		digitalWrite(PIN_LED_LATCH, LOW);
		step = 0;
		break;

	default:
		if (step % states_per_led == 0) {
			// ready the clock and set the data
			digitalWrite(PIN_LED_CLK, LOW);
			int bit_number_for_led = step / states_per_led;
			int bit_val = (1 & (leds_state >> bit_number_for_led));
			digitalWrite(PIN_LED_SERIAL, bit_val ? HIGH : LOW);
		} else {
			// clock out the data we set
			digitalWrite(PIN_LED_CLK, HIGH);
		}
		++step;
		break;
	}
}

void Eeg_lead_leds::update_all()
{
	step = 0;
	do {
		update_tick();
		delayMicroseconds(10);
	} while (step != 0);
}

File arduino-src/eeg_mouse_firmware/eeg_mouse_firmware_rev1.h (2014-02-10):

/* eeg_mouse_firmware_rev1.h */
#ifndef _EEG_MOUSE_FIRMWARE_REV1_H_
#define _EEG_MOUSE_FIRMWARE_REV1_H_

// IPIN_ is for pins that are inverted

// CS (chip select) is PB14, CANTX1/IO, PIN53
#define IPIN_CS 53

//  SCLK (serial clock) is PA27, SPCK, SPI PIN 3
// #define PIN_SCLK

// DIN (data in) is  PA26, MOSI, SPI PIN 4
// #define PIN_DIN

// DOUT (data out) is PA25, MISO, SPI PIN 1
// #define PIN_DOUT

// CLKSEL (clock select) is PC14, PIN 49
#define PIN_CLKSEL 49

// RESET is PC15, PIN 48 (was PIN 47 in rev0)
#define IPIN_RESET 48

// PWDN (power down) is PC16, PIN 47 (was PIN 48 in rev0)
#define IPIN_PWDN 47

// START is PC17, PIN 46
#define PIN_START 46

// DRDY (data ready) is PC18, PIN 45
#define IPIN_DRDY 45

// LED_ENABLE is PD6, PIN 29
#define IPIN_LED_ENABLE 29

// LED_LATCH is PD3, PIN 28
#define PIN_LED_LATCH 28

// LED_CLEAR is PD2, PIN 27
#define IPIN_LED_CLEAR 27

// LED_CLK (LED clock) is PD1, PIN 26
#define PIN_LED_CLK 26

// LED_SERIAL is PD0, PIN 25
#define PIN_LED_SERIAL 25

#endif /* _EEG_MOUSE_FIRMWARE_REV_1_H_ */

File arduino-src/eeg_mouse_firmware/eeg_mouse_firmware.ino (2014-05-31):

// modified from: http://www.windmeadow.com/node/38

#include <Arduino.h>
#include <SPI.h>

#include "eeg_mouse_firmware.h"
#include "eeg_lead_leds.h"
#include "ads1298.h"
#include "util.h"

// actual size today is 64, but a few extra will not hurt
#define DATA_BUF_SIZE 80

#ifndef LIVE_CHANNELS_NUM
#define LIVE_CHANNELS_NUM 8
#endif

#ifdef  _VARIANT_ARDUINO_DUE_X_
#define SPI_CLOCK_DIVIDER_VAL 21
#else
// #define SPI_CLOCK_DIVIDER_VAL SPI_CLOCK_DIV4
#define SPI_CLOCK_DIVIDER_VAL SPI_CLOCK_DIV8
#endif

#ifdef _VARIANT_ARDUINO_DUE_X_
#if ARDUINO_DUE_USB_PROGRAMMING == 1
#define SERIAL_OBJ Serial
#else // default to the NATIVE port
#define SERIAL_OBJ SerialUSB
#endif
#endif

#ifndef SERIAL_OBJ
#define SERIAL_OBJ Serial
#endif

// global variables
char setup_2_run;
char in_byte;
int led_status;
unsigned long last_blink;
unsigned long blink_interval_millis;
#if EEG_MOUSE_HARDWARE_VERSION != 0
Eeg_lead_leds lead_leds;
#endif
bool shared_negative_electrode = true;

#define LED_PIN 13
#define BLINK_INTERVAL_SETUP 100;
#define BLINK_INTERVAL_WAITING 500;
#define BLINK_INTERVAL_SENDING 2000;

void adc_send_command(int cmd)
{
	digitalWrite(IPIN_CS, LOW);
	SPI.transfer(cmd);
	delayMicroseconds(1);
	digitalWrite(IPIN_CS, HIGH);
}

byte adc_rreg(int reg)
{
	byte val;

	digitalWrite(IPIN_CS, LOW);

	SPI.transfer(ADS1298::RREG | reg);
	SPI.transfer(0);	// number of registers to be read/written – 1
	val = SPI.transfer(0);

	delayMicroseconds(1);
	digitalWrite(IPIN_CS, HIGH);

	return val;
}

void adc_wreg(int reg, int val)
{
	digitalWrite(IPIN_CS, LOW);

	SPI.transfer(ADS1298::WREG | reg);
	SPI.transfer(0);	// number of registers to be read/written – 1
	SPI.transfer(val);

	delayMicroseconds(1);
	digitalWrite(IPIN_CS, HIGH);
}

void read_data_frame(ADS1298::Data_frame * frame)
{
	digitalWrite(IPIN_CS, LOW);
	for (int i = 0; i < frame->size; ++i) {
		frame->data[i] = SPI.transfer(0);
	}
	delayMicroseconds(1);	// is this needed?
	digitalWrite(IPIN_CS, HIGH);
}

void update_leadoff_led_data(const ADS1298::Data_frame & frame)
{
	for (int channel = 0; channel < LIVE_CHANNELS_NUM; ++channel) {
		bool leadoff_p = frame.loff_statp(channel);
		lead_leds.set_green_positive(channel, !leadoff_p);
		lead_leds.set_yellow_positive(channel, leadoff_p);

		// if the negative electrodes are shared, use only the first LED.
		if (channel == 0 || !shared_negative_electrode) {
			bool leadoff_n = frame.loff_statn(channel);
			lead_leds.set_green_negative(channel, !leadoff_n);
			lead_leds.set_yellow_negative(channel, leadoff_n);
		} else {
			lead_leds.set_green_negative(channel, false);
			lead_leds.set_yellow_negative(channel, false);
		}
	}
}

void update_bias_ref(const ADS1298::Data_frame & frame)
{
	using namespace ADS1298;

	static uint8_t last_loff_statp = 0xFF;
	static uint8_t last_loff_statn = 0xFF;
	static unsigned samples_since_last_bias_change = 0;
	const unsigned min_samples_between_bias_changes = 100;

	uint8_t loff_statp = frame.loff_statp();
	uint8_t leads_on_p = ~loff_statp;
	uint8_t loff_statn = frame.loff_statn();
	uint8_t leads_on_n = ~loff_statn;

	if (shared_negative_electrode) {
		loff_statn |= 0x01;	// count only the single shared electrode
	}
	// if the lead-off status has changed...
	if (samples_since_last_bias_change >= min_samples_between_bias_changes
	    && (last_loff_statp != loff_statp
		|| last_loff_statn != loff_statn)) {

		// Send SDATAC Command (Stop Read Data Continuously mode)
		// TODO: starting and stopping the data collection like this will
		// create a glitch in all channels of the recording whenever the
		// leadoff status of any channel changes.  This could be fixed by
		// capturing all data in single-shot mode, triggered by an interrupt.
		adc_send_command(SDATAC);

		// Use only the leads that are connected to drive the bias electrode.
		adc_wreg(RLD_SENSP, leads_on_p);
		adc_wreg(RLD_SENSN, leads_on_n);

		// Put the Device Back in Read DATA Continuous Mode
		adc_send_command(RDATAC);

		last_loff_statp = loff_statp;
		last_loff_statn = loff_statn;
		samples_since_last_bias_change = 0;
	} else {
		++samples_since_last_bias_change;
	}
}

// if this becomes more flexible, we may need to pass in
// the byte_buf size, but for now we are safe to skip it
void format_data_frame(const ADS1298::Data_frame & frame, char *byte_buf)
{
	uint8_t in_byte;
	unsigned int pos = 0;

	byte_buf[pos++] = '[';
	byte_buf[pos++] = 'g';
	byte_buf[pos++] = 'o';
	byte_buf[pos++] = ']';

	for (int i = 0; i < frame.size; ++i) {
		in_byte = frame.data[i];
		to_hex(in_byte, byte_buf + pos);
		pos += 2;
	}

	byte_buf[pos++] = '[';
	byte_buf[pos++] = 'o';
	byte_buf[pos++] = 'n';
	byte_buf[pos++] = ']';
	byte_buf[pos++] = '\n';
	byte_buf[pos++] = 0;
}

void serial_print_error(const char *msg)
{
	SERIAL_OBJ.print("[oh]");
	SERIAL_OBJ.print(msg);
	SERIAL_OBJ.print("[no]\n");
}

void wait_for_drdy(const char *msg, int interval)
{
	int i = 0;
	while (digitalRead(IPIN_DRDY) == HIGH) {
		if (i < interval) {
			continue;
		}
		i = 0;
		serial_print_error(msg);
	}
}

void blink_led(void)
{
	unsigned long now = millis();

	if ((now - last_blink) > blink_interval_millis) {
		led_status = (led_status == HIGH) ? LOW : HIGH;
		digitalWrite(LED_PIN, led_status);
		last_blink = now;
	}
}

void setup(void)
{
	setup_2_run = 0;
	in_byte = 0;
	led_status = HIGH;
	last_blink = 0;
	blink_interval_millis = BLINK_INTERVAL_SETUP;
	pinMode(LED_PIN, OUTPUT);
}

void setup_2(void)
{
	using namespace ADS1298;
	int i;

	// initialize the USB Serial connection
	SERIAL_OBJ.begin(230400);

	// set the LED on
	pinMode(13, OUTPUT);
	digitalWrite(13, HIGH);

	pinMode(IPIN_CS, OUTPUT);
#if EEG_MOUSE_HARDWARE_VERSION == 0
	pinMode(PIN_SCLK, OUTPUT);
	pinMode(PIN_DIN, OUTPUT);
	pinMode(PIN_DOUT, INPUT);
#endif

	pinMode(PIN_CLKSEL, OUTPUT);
	pinMode(PIN_START, OUTPUT);
	pinMode(IPIN_RESET, OUTPUT);
	pinMode(IPIN_PWDN, OUTPUT);
	pinMode(IPIN_DRDY, INPUT);

#if EEG_MOUSE_HARDWARE_VERSION != 0
	lead_leds.begin();
	// while waiting for the device to power up,
	// sequentially light the green LEDs for IN1P through IN8P
	for (i = 0; i < Eeg_lead_leds::num_channels; ++i) {
		lead_leds.set_green_positive(i, true);
		lead_leds.update_all();
		delay(50);
	}
	// then IN1N through IN8N
	for (i = 0; i < Eeg_lead_leds::num_channels; ++i) {
		lead_leds.set_green_negative(i, true);
		lead_leds.update_all();
		delay(50);
	}
#endif

	SPI.begin();

	SPI.setBitOrder(MSBFIRST);
	SPI.setClockDivider(SPI_CLOCK_DIVIDER_VAL);
	SPI.setDataMode(SPI_MODE1);

	//digitalWrite(IPIN_CS, LOW);
	digitalWrite(PIN_CLKSEL, HIGH);

	// Wait for 20 microseconds Oscillator to Wake Up
	delay(1);		// we'll actually wait 1 millisecond

	digitalWrite(IPIN_PWDN, HIGH);
	digitalWrite(IPIN_RESET, HIGH);

	// Wait for 33 milliseconds (we will use 100 millis)
	//  for Power-On Reset and Oscillator Start-Up
	delay(100);

	// Issue Reset Pulse,
	digitalWrite(IPIN_RESET, LOW);
	// actually only needs 1 microsecond, we'll go with milli
	delay(1);
	digitalWrite(IPIN_RESET, HIGH);
	// Wait for 18 tCLKs AKA 9 microseconds, we use 1 millisec
	delay(1);

	// Send SDATAC Command (Stop Read Data Continuously mode)
	adc_send_command(SDATAC);

	// All GPIO set to output 0x0000
	// (floating CMOS inputs can flicker on and off, creating noise)
	adc_wreg(GPIO, 0x00);

	// Power up the internal reference and wait for it to settle
	adc_wreg(CONFIG3,
		 RLDREF_INT | PD_RLD | PD_REFBUF | VREF_4V | CONFIG3_const);
	delay(150);

	// Use lead-off sensing in all channels (but only drive one of the
	// negative leads if all of them are connected to one electrode)
	adc_wreg(CONFIG4, PD_LOFF_COMP);
	adc_wreg(LOFF, COMP_TH_80 | ILEAD_OFF_12nA);
	adc_wreg(LOFF_SENSP, 0xFF);
	adc_wreg(LOFF_SENSN, shared_negative_electrode ? 0x01 : 0xFF);

	// Write Certain Registers, Including Input Short
	// Set Device in HR Mode and DR = fMOD/1024
	//adc_wreg(CONFIG1, HR | LOW_POWR_500_SPS);
	adc_wreg(CONFIG1, HR | LOW_POWR_250_SPS);
	adc_wreg(CONFIG2, INT_TEST);	// generate internal test signals

	// If we want to share a single negative electrode, tie the negative
	// inputs together using the BIAS_IN line.
	uint8_t mux = shared_negative_electrode ? RLD_DRN : ELECTRODE_INPUT;

	// connect the negative channel to the (shared) BIAS_IN line
	// Set the first LIVE_CHANNELS_NUM channels to input signal
	for (i = 1; i <= LIVE_CHANNELS_NUM; ++i) {
		adc_wreg(CHnSET + i, mux | GAIN_12X);
		// adc_wreg(CHnSET + i, TEST_SIGNAL | GAIN_12X);
	}
	// Set all remaining channels to shorted inputs
	for (; i <= 8; ++i) {
		adc_wreg(CHnSET + i, SHORTED | PDn);
	}

	digitalWrite(PIN_START, HIGH);
	wait_for_drdy("waiting for DRDY in setup", 1000);

	adc_send_command(RDATAC);
	blink_interval_millis = BLINK_INTERVAL_WAITING;
}

void check_for_ping_from_serial()
{
	using namespace ADS1298;
	byte version;
	int i = 0;
	char msg[40];

	if (SERIAL_OBJ.available() == 0) {
		return;
	}
	// read an available byte:
	in_byte = SERIAL_OBJ.read();

	if (in_byte != 0) {
		// Send SDATAC Command (Stop Read Data Continuously mode)
		adc_send_command(SDATAC);

		msg[i++] = '[';
		msg[i++] = 'i';
		msg[i++] = 't';
		msg[i++] = ']';

		version = adc_rreg(ADS1298::ID);
		msg[i++] = 'c';
		msg[i++] = 'h';
		msg[i++] = 'i';
		msg[i++] = 'p';
		msg[i++] = ' ';
		msg[i++] = 'i';
		msg[i++] = 'd';
		msg[i++] = ':';
		msg[i++] = ' ';
		msg[i++] = '0';
		msg[i++] = 'x';
		to_hex(version, msg + i);
		i += 2;

		msg[i++] = '[';
		msg[i++] = 'i';
		msg[i++] = 's';
		msg[i++] = ']';
		msg[i++] = '\n';
		msg[i++] = '\0';
		SERIAL_OBJ.print(msg);

		// Put the Device Back in Read DATA Continuous Mode
		adc_send_command(RDATAC);
		blink_interval_millis = BLINK_INTERVAL_SENDING;
	}
}

void loop(void)
{
	char byte_buf[DATA_BUF_SIZE];

	blink_led();
	lead_leds.update_tick();

	if (!setup_2_run) {
		setup_2();
		setup_2_run = 1;
	}
	// read the next frame, if available
	ADS1298::Data_frame frame;
	if (digitalRead(IPIN_DRDY) == LOW) {
		read_data_frame(&frame);
		update_leadoff_led_data(frame);
		update_bias_ref(frame);
		if (in_byte != 0) {
			format_data_frame(frame, byte_buf);
			SERIAL_OBJ.print(byte_buf);
		}
	}
	// wait for a non-zero byte as a ping from the computer
	// loop until data available
	if (in_byte == 0) {
		check_for_ping_from_serial();
	}
}

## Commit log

2011-11-26 added schematic file
    [eeg-mouse.sch]
2011-11-26 add inputs
    [eeg-mouse.sch]
2011-11-26 connecting pins 17-32
    [eeg-mouse.sch]
2011-11-26 pins 33 t/m 48
    [eeg-mouse.sch]
2011-11-26 pins 49 t/m 64
    [eeg-mouse.sch]
2011-11-26 adjust comment
    [eeg-mouse.sch]
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2011-11-27 added power connectors, all the ins and outs
    [eeg-mouse.sch]
2011-11-27 number our parts
    [eeg-mouse.sch]
2011-11-27 fix missing connections; add power flags
    [eeg-mouse.sch]
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2011-11-27 added a mouser BOM for parts
    [eeg-mouse.csv, eeg-mouse.sch]
2011-12-03 change VCAP1 to polarized capacitor
    [eeg-mouse.sch]
2011-12-03 initial component layout
    [eeg-mouse.brd]
2011-12-10 unswap input groups
    [eeg-mouse.brd]
2011-12-10 adjust layout for pcb
    [eeg-mouse.brd]
2011-12-10 adjust layout for pcb some more
    [eeg-mouse.brd]
2011-12-10 flipped capacitor to fix overlapping labels
    [eeg-mouse.sch]
2011-12-17 breadboard layout, tracks 1-16
    [eeg-mouse.brd]
2011-12-17 change traces from back to front
    [eeg-mouse.brd]
2011-12-17 fix track to line up with pin 16
    [eeg-mouse.brd]
2011-12-17 clarify voltage connection for AVDD1
    [eeg-mouse.sch]
2011-12-17 clarify voltage connection for AVSS1
    [eeg-mouse.sch]
2011-12-17 adjust board layout in prep for tracks
    [eeg-mouse.brd]
2011-12-18 rearrange south capacitors
    [eeg-mouse.brd]
2011-12-18 move references so they are not overlapping
    [eeg-mouse.brd]
2011-12-18 add traces pins->capacitors
    [eeg-mouse.brd]
2011-12-18 traces for pins on north side
    [eeg-mouse.brd]
2011-12-18 fixed traces on west side
    [eeg-mouse.brd]
2012-01-07 connect up east side of chip
    [eeg-mouse.brd]
2012-01-07 connect 3.3v
    [eeg-mouse.brd]
2012-01-07 hook up west side tracks
    [eeg-mouse.brd]
2012-01-07 hook up remaining grounds
    [eeg-mouse.brd]
2012-01-07 fix track errors
    [eeg-mouse.brd]
2012-01-07 add board edges
    [eeg-mouse.brd]
2012-01-07 create ground and power planes
    [eeg-mouse.brd]
2012-01-07 ground plane cleanup
    [eeg-mouse.brd]
2012-01-07 ground plane cleanup part 2
    [eeg-mouse.brd]
2012-01-07 label connector pins
    [eeg-mouse.brd]
2012-01-07 tidy up zones
    [eeg-mouse.brd]
2012-01-07 reduce ground plane interruptions
    [eeg-mouse.brd]
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2012-01-09 changed solder mask clearance for ADS1298
    [eeg-mouse.brd]
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2012-03-25 fix DIN label (should not have been inverted)
    [eeg-mouse.brd]
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2012-11-07 remove generated file signal-with-noise.csv
    [signal-with-noise.csv]
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2013-03-30 short DAISY_IN to DGND as unused
    [arduino-ads129x.sch]
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2013-03-30 made filtering capacitors more consistent
    across the board we are using non-polarized 10uF and 100nF
    now for power filtering, except on ADS1299 VCAP1 which is
    100uF and polarized as recommended by datasheet due to noise
    concerns.
    [arduino-ads129x.sch]
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2013-05-05 fix labels on SAM3X component
    [arduino-ads129x.sch]
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2013-05-18 replace serial port net-labels with plain text
    [arduino-ads129x.sch]
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2013-05-27 improve robustness and leakage for bnc shield
    [bnc-shield.sch]
2013-05-27 fixed 2.5V regulator resistors
    [bnc-shield.sch]
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2013-06-01 replace 3.3v with buck regulator, add LC filter
    [arduino-ads129x.sch]
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2013-06-02 replace criss-crossed lines with labels
    [arduino-ads129x.sch]
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2013-06-02 fix "no connect" misplacement
    [arduino-ads129x.sch]
2013-06-02 fix capitalization: SI86xx -> Si86xx
    [arduino-ads129x.sch]
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2013-06-08 fix typo
    [arduino-ads129x.sch]
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2013-06-08 replace protection diodes on USB with USBLC6
    [arduino-ads129x.sch]
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2013-06-09 fix wrongly labled pin
    [arduino-ads129x.sch]
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2013-06-09 fix floating labels
    [arduino-ads129x.sch]
2013-06-09 fix more labels
    [arduino-ads129x.sch]
2013-06-09 fix yet another label
    [arduino-ads129x.sch]
2013-06-09 several little fixups with wires and labels
    [arduino-ads129x.sch]
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2013-06-09 more schematic fixups and tidy
    [arduino-ads129x.sch]
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2013-06-14 Revert "added zener diodes to provide some overvoltage protection"
    This reverts commit 6d3495b4e318b6e9bb2e5f0eeab4ae7c38ce5538.
    [arduino-ads129x.sch]
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2013-06-15 replace preregulator with crowbar circuits
    [arduino-ads129x.sch]
2013-06-15 swap resistors in crowbar circuits
    [arduino-ads129x.sch]
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2013-06-15 replace crowbar capacitors for stability
    [arduino-ads129x.sch]
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2013-06-15 fix resistor name
    [arduino-ads129x.sch]
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2013-06-21 Fixed patch shield to pass ERC
    [patch-shield-analog.sch]
2013-06-22 Fixed digital part of patch shield to pass ERC
    [patch-shield-digital.sch]
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2013-06-24 added series resistors for noise reduction
    [arduino-ads129x.sch]
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2013-06-29 fix inductor label rotation
    [arduino-ads129x.sch]
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2013-06-29 Fix addition inductor label rotations
    [arduino-ads129x.sch]
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2013-06-29 fix pullup resistor for JTAG TMS
    [arduino-ads129x.brd, arduino-ads129x.sch]
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2013-07-13 fix typo ADS192x to ADS129x
    [arduino-ads129x.brd, arduino-ads129x.sch]
2013-07-13 swap order of lines through isolators to avoid as much crossing
    [arduino-ads129x.brd, arduino-ads129x.sch]
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2013-07-20 fix inverted FTDI connector
    [arduino-ads129x.brd]
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2013-07-27 fix grid origin
    [arduino-ads129x.brd]
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2013-07-31 add voltage translator for digital BNC connectors, fix some ERC errors
    [bnc-shield.sch]
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2013-08-09 fix accidental connection of ADS1299 pin 31 to AGND via zone filling, increment version to 1.1
    [arduino-ads129x.brd]
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2013-08-27 fix patch-shield-digital gerber files by refilling zones
    [patch-shield-digital-Back.gbl, patch-shield-digital-Front.gtl, patch-shield-digital-Mask_Back.gbs, patch-shield-digital-Mask_Front.gts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]
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2013-11-09 arduino-ads129x.brd : Fixed CAT24C128 footprint
    [arduino-ads129x.brd]
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2014-01-25 fix D1 footprint and tracks
    D1 should have been DO214 with cathode on the north side
    BZG03C-Series datasheet: http://www.vishay.com/docs/85593/bzg03c.pdf
    [arduino-ads129x.brd, arduino-ads129x.sch]
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2014-04-20 Switch to 2D primitives which are extruded to 3D
    Our laser cut parts are 2D patterns that are used to cut a 3D sheet, and
    we need these 2D patterns (e.g. DXF files) for the laser cutter. We
    could get these 2D patterns either by taking the projection of a 3D
    object, or by creating a 2D object directly. Either one should work,
    but starting with the 2D pattern should be more computationally
    efficient and OpenSCAD (version 2013.05.28) is crashing when I try to
    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
    [rev1_case_v1.scad]
2014-04-20 Expand screw holes to be proper size for #6 screws
    Our design had 3.6 mm screw holes that were a bit small for #6 screws,
    but Gold Phoenix PCB appears to have drilled larger 3.8 mm holes for our
    prototype boards (which is the size Machinery's Handbook recommends for
    a free clearance fit for this screw size). To save us from problems
    with future board runs, this check in expands the holes in the design to
    match the 3.8 mm size of the holes on the prototype boards.
    [arduino-ads129x.brd, bnc-shield.brd, patch-shield-analog.brd, patch-shield-digital.brd]
2014-04-20 Review, measure, and adjust hole sizes and positions
    Reviewed and adjusted all slot and hole sizes and positions. Numbers
    were measured from kicad (with calculations done in ipython), and then
    checked for gross errors by exporting the dxf from openscad and an
    svg from kicad and overlaying the two.
    [rev1_case_v1.scad]
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2014-04-20 Round most sharp corners
    Internal sharp corners can cause stress concentration (leading to
    cracks), and external sharp corners can be uncomfortable to handle.
    This check in rounds the corners on the slots and the corners of the top
    and bottom plate.
    [rev1_case_v1.scad]
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2014-04-26 fix syntax error
    [rev1.scad]
2014-04-26 Allow kerf to be specified.
    The slot cut by a tool like a laser cutter has a finite width (known as
    the kerf of the tool), so that holes and slots will be wider than they
    are in the pattern and cut out objects will be smaller than they are in
    the pattern. We correct for this by moving the center of the cutting
    line inward (for holes) or outward (for cut out shapes) so that the edge
    of the cut line will be in the correct place.
    [rev1_case_v1.scad, rev1_case_v1_dimensions.scad, rev1_case_v1_pattern.scad]
2014-04-26 Fix draw order.
    OpenSCAD does not sort transparent objects from back to front when
    drawing, so sometimes you can't see one transparent object behind
    another. The bottom of the case was being draw after the top, so
    it wasn't visible through the top of the case when looking from above
    (the common case); drawing the bottom first fixes this (but causes
    drawing problems when viewing the device from the bottom, the less
    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
    [rev1_case_v1.scad]
2014-04-26 Fix horizontal header pin height, minor cleanups.
    [rev1.scad, rev1_case_v1.scad]
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2014-05-03 replace magic constant with descriptive name
    [rev1_case_v1.scad]
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

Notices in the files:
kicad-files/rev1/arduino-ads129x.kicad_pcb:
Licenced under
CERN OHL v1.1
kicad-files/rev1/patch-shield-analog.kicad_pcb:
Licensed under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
